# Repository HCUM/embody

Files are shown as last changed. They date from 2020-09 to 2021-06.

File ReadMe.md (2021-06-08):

# EMBody: A Data-Centric Toolkit for EMG-Based Interface Prototyping and Experimentation

This repository contains EMBody, a data-centric toolkit for rapid prototyping and experimentation of EMG-based interfaces. You can find the associated publication [here](https://dl.acm.org/doi/10.1145/3457142). Feel free to watch our short teaser video below. You can additionally find a detailed [instructional video](./manual/manual.mp4) as part of the [manual](./manual).

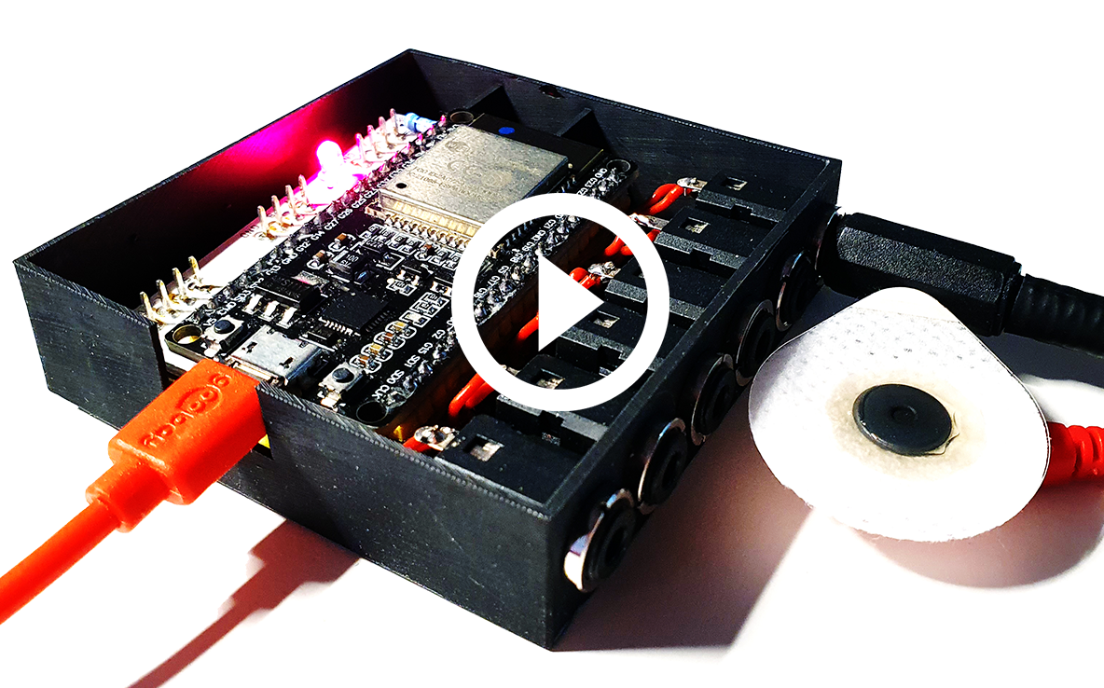
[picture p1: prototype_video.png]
System teaser|70% (https://jakob-karolus.de/publications/karolus21embody.mp4)


## About
EMBody is a toolkit, which is developed at LMU Munich. It is financially supported by the European Union's Horizon 2020 Programme under ERCEA grant no. 683008 AMPLIFY.

The toolkit consists of a hardware prototype that can record electrical potentials (e.g. via surface electrodes), convert these in a digital representation, and stream them over an available WiFi connection. This is complemented by an accompanying [software application](./embody), that receives the signal and provides an interpretation of the data.

EMBody's main use case is recording electromyograms (EMG) via surface electrodes. We envision that the toolkit enables creators to rapidly begin their journey into EMG-based interfaces. This repository contains all the necessary resources to build the system from scratch. Please feel free to contact us in case of questions.

## Hardware ressources
* Circuit board layouts and cases: see [Casing](./casings) and [Circuits](./circuits) for files
* Short [assembly description](./circuits)
* Firmware for ESP32 microcontroller: see [Firmware](./esp_firmware)

## Software application
* python application [EMBody](./embody) connecting to the prototype, see the [Manual](./manual) for a detailed operation manual and workflow including the instructional video

## Citing EMBody

Below are the BibTex entries to cite EMBody
```
@article{karolusEmbody2021,
author = {Karolus, Jakob and Kiss, Francisco and Eckerth, Caroline and Viot, Nicolas and Bachmann, Felix and Schmidt, Albrecht and Wo\'{z}niak, Pawe\l W.},
title = {EMBody: A Data-Centric Toolkit for EMG-Based Interface Prototyping and Experimentation},
year = {2021},
issue_date = {June 2021},
publisher = {Association for Computing Machinery},
address = {New York, NY, USA},
volume = {5},
number = {EICS},
doi = {10.1145/3457142},
url = {https://github.com/HCUM/embody},
journal = {Proc. ACM Hum.-Comput. Interact.},
month = may,
articleno = {195},
numpages = {29}
}
```

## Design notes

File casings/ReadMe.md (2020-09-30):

# Casing files
STL files for the prototype's casing as well as lid to cover the components.
Additionally, a scene file from 3ds Max is provided for customization.

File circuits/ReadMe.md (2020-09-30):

# Circuit files
## INA2321Bioamp_2018-10-30.zip
Gerber files for adapted bio amplifier (see https://github.com/BigCorvus/2-Channel-Biopotential-Amp) and corresponding bom list.
## adapter19to3x4_v3_2020-05-04.zip
Gerber files for custom adapter board connecting three amplifiers to a ESP-32 microcontroller.

# Hardware Assembly Instruction

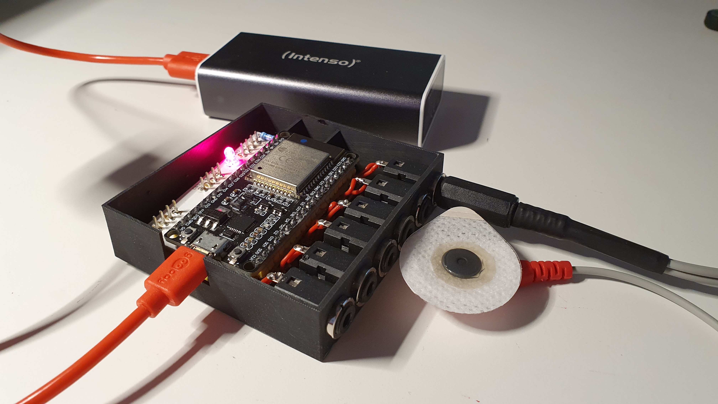
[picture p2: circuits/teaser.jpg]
Wireless EMG Sensor


## General connection diagram

This is the general diagram of the hardware.

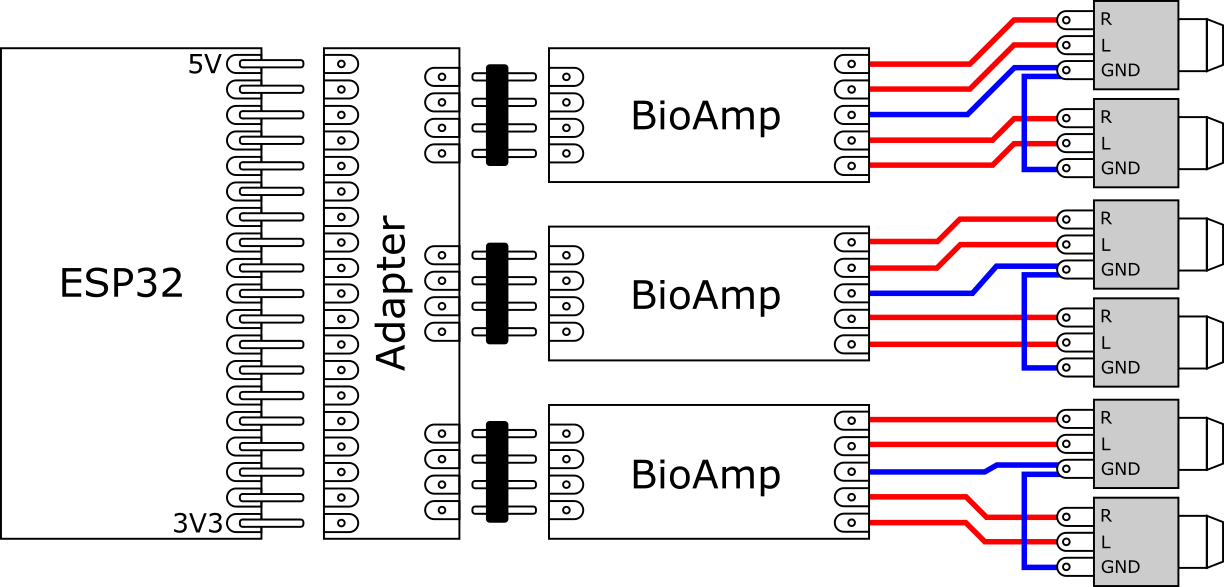
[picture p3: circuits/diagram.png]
Circuit diagram


Follow the instructions below for a guided assembly tutorial.

## How to assemble the EMG hardware
The process is easy and requires minimal skills.
You will need the following tools:

* Soldering iron
* Solder
* Tweezers
* Wire-cutter
* Permanent marker

And the following components:

* ESP32 board x 1
* Bioamplifier x 3
* Adapter board x 1
* Insulated copper wire
* Heat shrink tubing (14mm) 
* LED 5 mm x 1
* 100 Ohm axial resistor x 1
* Header with 4 pins x 3
* Stereo female audio jacks (3.5mm) x 6 - [This model](http://www.farnell.com/datasheets/2645331.pdf) fits in the 3D case
* 3D printed case

### Step 1: solder cables to Bioamplifier board
Cut pieces of cable around 5 cm long, peel one end, and solder them to the five pads on the input side of the Bioamplifier (marked in the image below). The cables should come out on the upper side of the board. Repeat for all Bioamplifier boards.

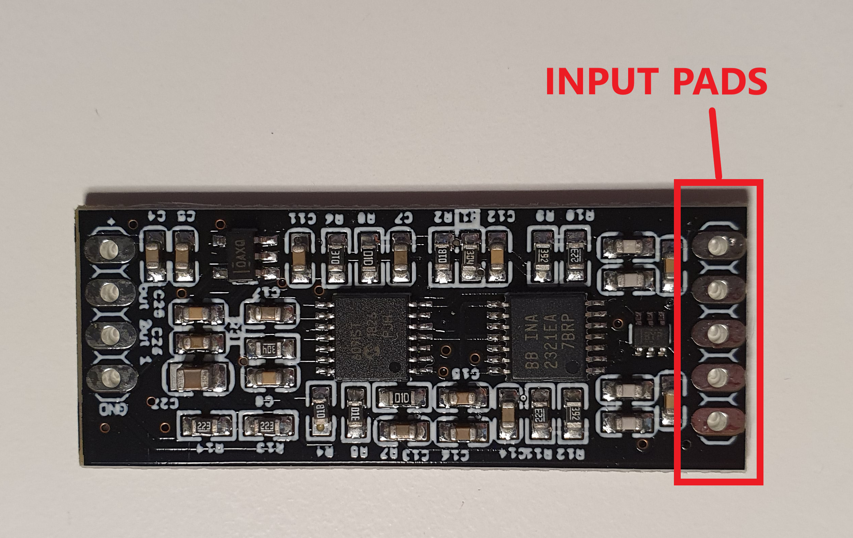
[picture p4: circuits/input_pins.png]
Input pads of the Bioamplifier


### Step 2: insulate the Bioamplifier board
Insert the board through a piece of heat shrink tube of adequate length to cover the components but leaving the pads free. Alternatively, use electrical tape if heat shrink tube is not available. Repeat for all Bioamplifier boards.

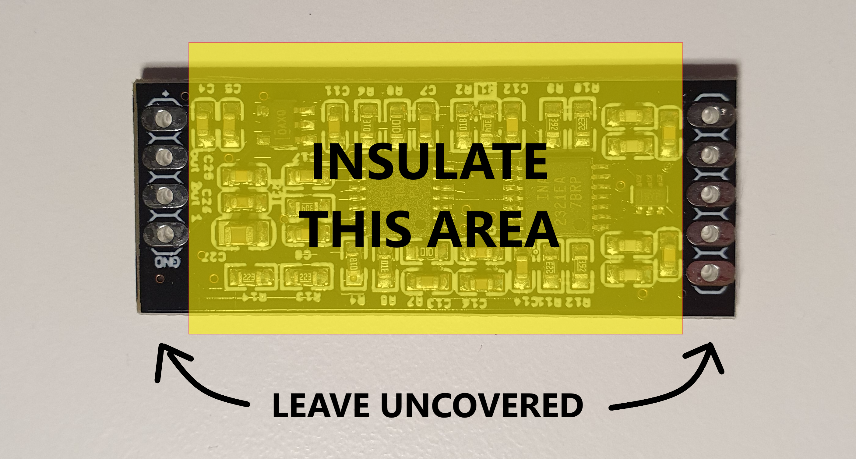
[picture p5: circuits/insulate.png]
Insulate the components


### Step 3: solder headers to Bioamplifier board
Solder the 4-pin headers on the upper side of the board, as shown in the image below. Repeat for all Bioamplifier boards. 

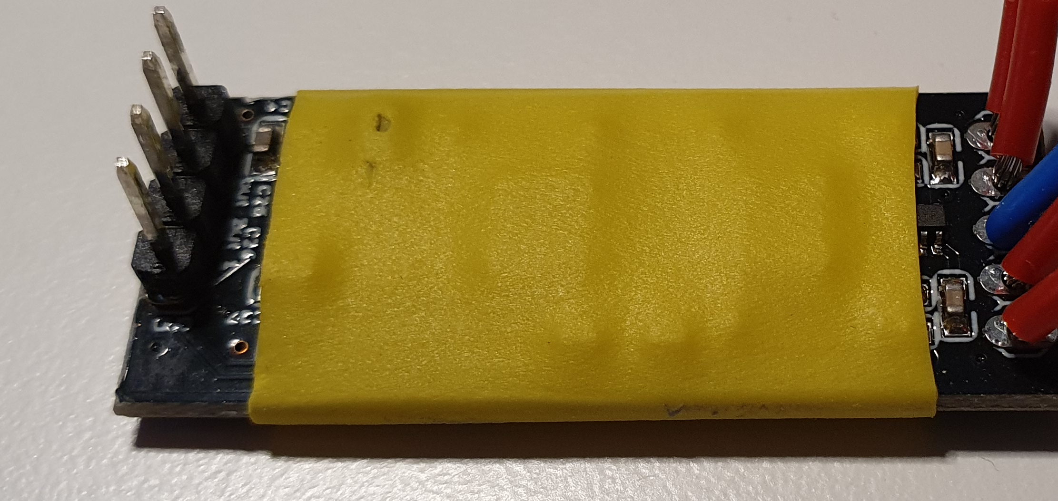
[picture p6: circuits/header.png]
Solder the header pins


### Step 3: solder resistor and LED to Adapter board
Solder the resistor on the upper side of the board, as shown in the picture. Solder the LED on the same side. Remove the protruding pins on the opposite side.

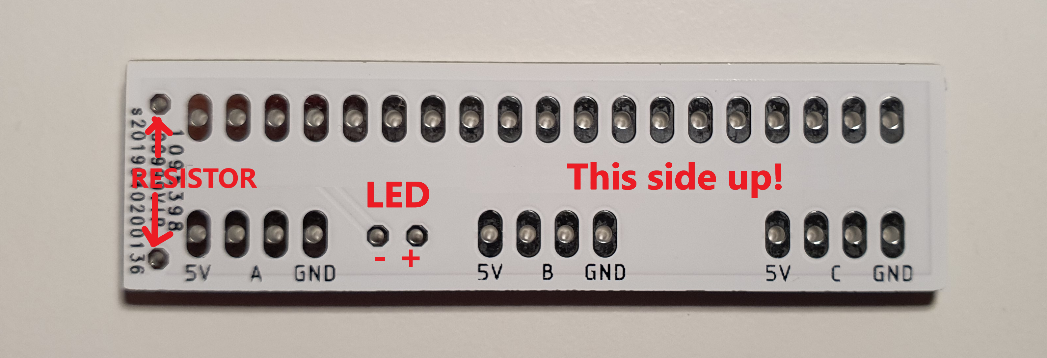
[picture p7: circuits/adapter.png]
Solder LED and resistor


### Step 4: solder ESP32 to Adapter board
Solder the 19 pins of the left side of the ESP32 to the Adapter board (see left image from step 5).

### Step 5: solder Bioamplifiers to the Adapter board
Solder all Bioamplifiers to the Adapter board. The Adapter board should face up, on top of the Bioamplifiers. 

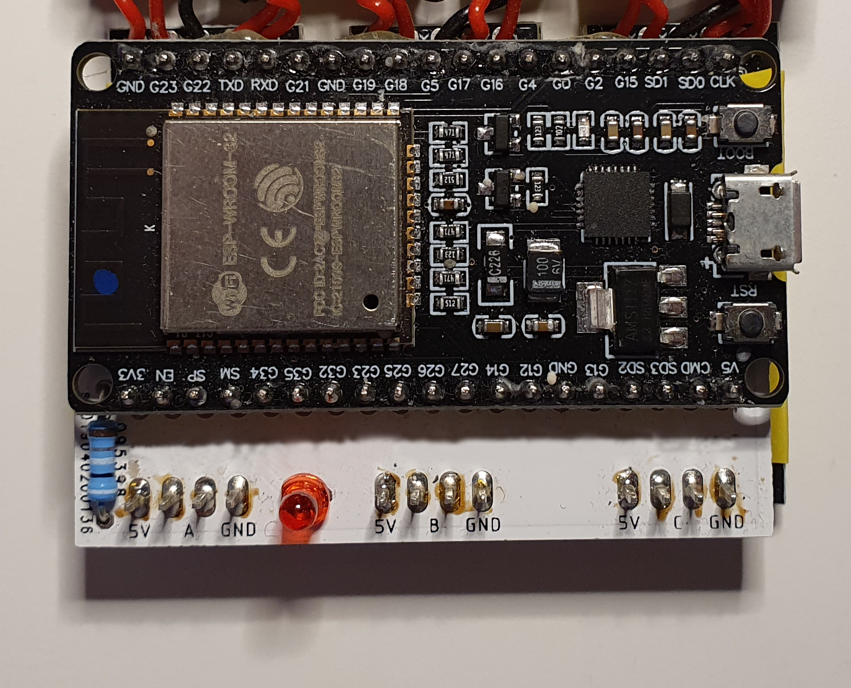
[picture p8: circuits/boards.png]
Top view of assembled boards
||Bottom view of assembled boards|

### Step 6: solder connectors
Position the boards and the audio connectors in the 3D-printed case, and use a permanent marker to mark the length of the wires where they touch the corresponding pad of the connector (use as reference the image from Step 7).
Remove all parts from the case. Cut and peel the cables using the marks as reference. Using additional pieces of wire, solder the ground pin of the audio connectors together in pairs, so you have three pairs of connectors. Solder the cables from the Bioamplifiers to the connectors.

### Step 7: flash and finish
Position the hardware in the case, as shown in the image below.
Close the case. The device is ready to flash! 

Finished device

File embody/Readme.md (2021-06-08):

# EMBody software application

**For a complete manual on EMBody's workflow, please refer to the [Manual](../manual), which also includes an instructional video.**

Run "python Main.py" to start the application. This software is based on Python 3.6 and the following libraries: 
* wxPython
* matplotlib
* pandas
* numpy
* scipy
* sklearn
* pylsl

It provides a GUI split into different views, that interact with each other: Setup, Calibration and Liveview, as well as a logic backend for stream and classification handling, communicating over StreamEvents.
Note that developers can provide additional functionality by adding more views or substituting stream handling (StreamHandler.py). Of special interest in this case should also be the ClassificationManager.py handling classification for the incoming signal.
Developers are encouraged to change preprocessing, feature generation and classification algorithms if needed.

## Overview of EMBody's classification pipeline
Please refer to the paper and source code for additional information.

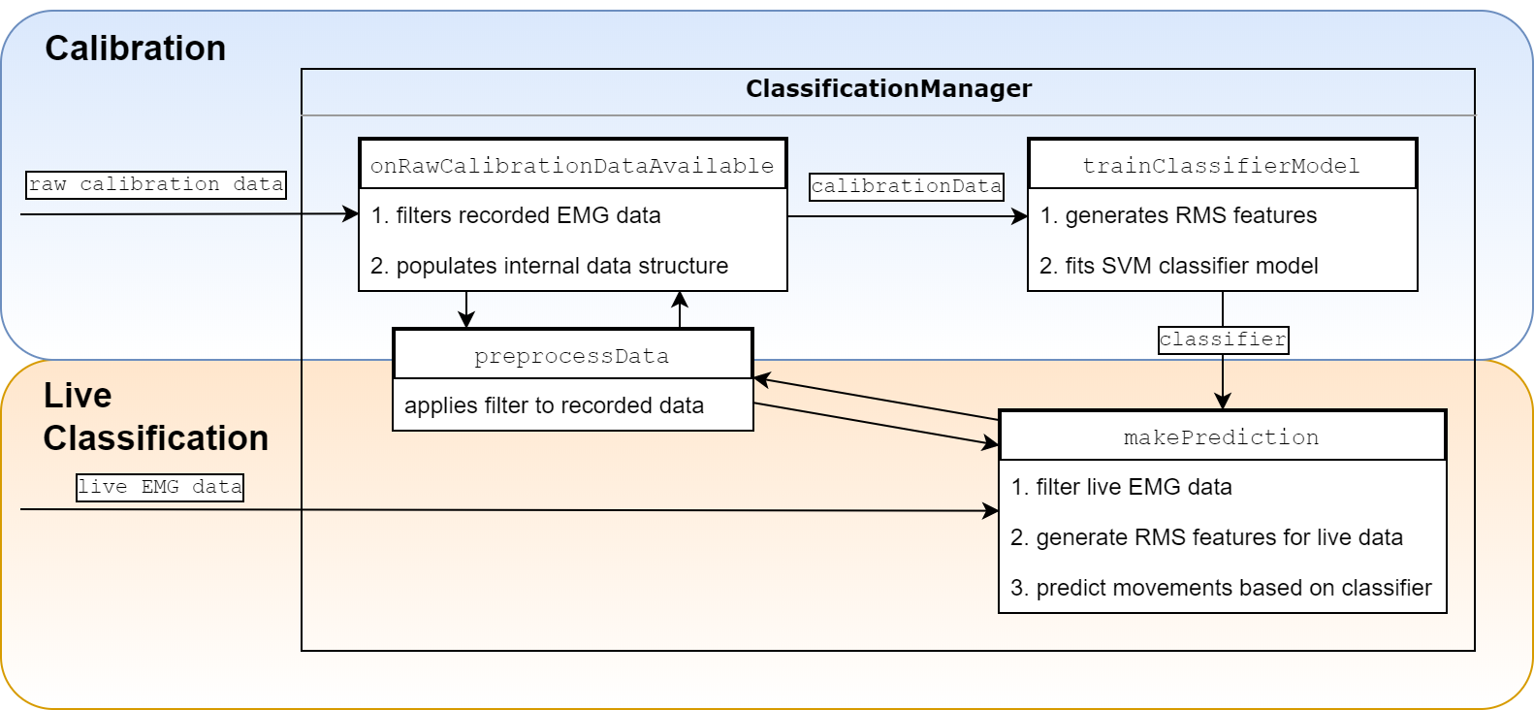
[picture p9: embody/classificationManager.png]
classificationManager


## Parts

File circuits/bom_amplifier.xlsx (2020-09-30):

Designator | Manufacturer Part Number | Quantity
R7, R8 | RC0603FR-07100KL | 2
C4, C5, C11, C15, C26 | CC0603KRX7R9BB104 | 5
C1, C2, C6, C9 | CC0603JRNPO9BN101 | 4
C3, C10, C25 | CC0603KRX7R9BB103 | 3
C27 | CC0805KKX5R8BB106 | 1
R5, R6 | RC0603FR-071ML | 2
R2, R4 | RC0603FR-071KL | 2
C8, C12 | CC0603KRX7R9BB102 | 2
C7, C13, C14, C16, C17 | CC0603KRX7R8BB105 | 5
R10, R11, R13, R14 | RC0603FR-0722KL | 4
R1, R3 | 0603SAF3003T5E | 2
R9, R12 | RC0603FR-073K9L | 2
U$1 | INA2321EA/250 | 1
U$3 | MCP609-I/ST | 1
IC2 | OPA333AIDBVT | 1
U$2 | TPD4E1B06DCKR | 1

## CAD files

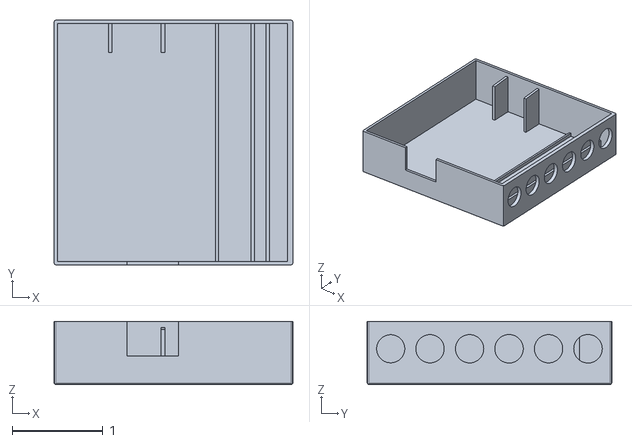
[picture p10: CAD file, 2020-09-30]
casings/emg_case_bottom.STL
2.63 x 2.69 x 0.694

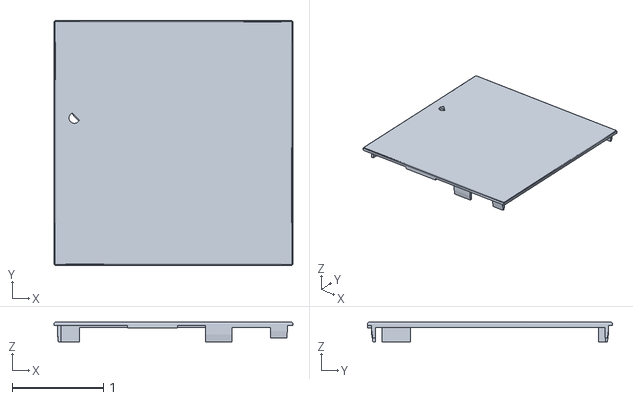
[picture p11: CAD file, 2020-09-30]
casings/emg_case_lid.STL
2.62 x 2.69 x 0.217

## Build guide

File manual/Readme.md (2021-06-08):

# EMBody: An Integrated Toolkit for EMG-Based Interface Prototyping

This manuals describe how to use the software toolkit to connect to an existing EMBody prototype and interpret the signal.
The software is based on Python 3.6 and the following libraries: wxPython, matplotlib, pandas, numpy, scipy, sklearn, pylsl (also refer to [EMBody Software](../embody)).
It provides a GUI split into different views, that interact with each other: Setup, Calibration and Liveview, as well as a logic backend for stream and classification handling, communicating over StreamEvents. Note that developers can provide additional functionality by adding more views or substituting stream handling (StreamHandler.py). Of special interest in this case should also be the ClassificationManager.py handling classification for the incoming signal. Developers are encouraged to change preprocessing, feature generation and classification algorithms if needed.
Details on hook methods and their purpose can be found in the paper (an overview is provided at [EMBody Software](../embody)).

EMBody already provides out-of-the-box functionality to calibrate and predict gestures recorded via EMG signals. This section outlines a typical workflow and gives detailed instructions for the individual views of the toolkit. The following video provides the same step by step guide for this workflow.

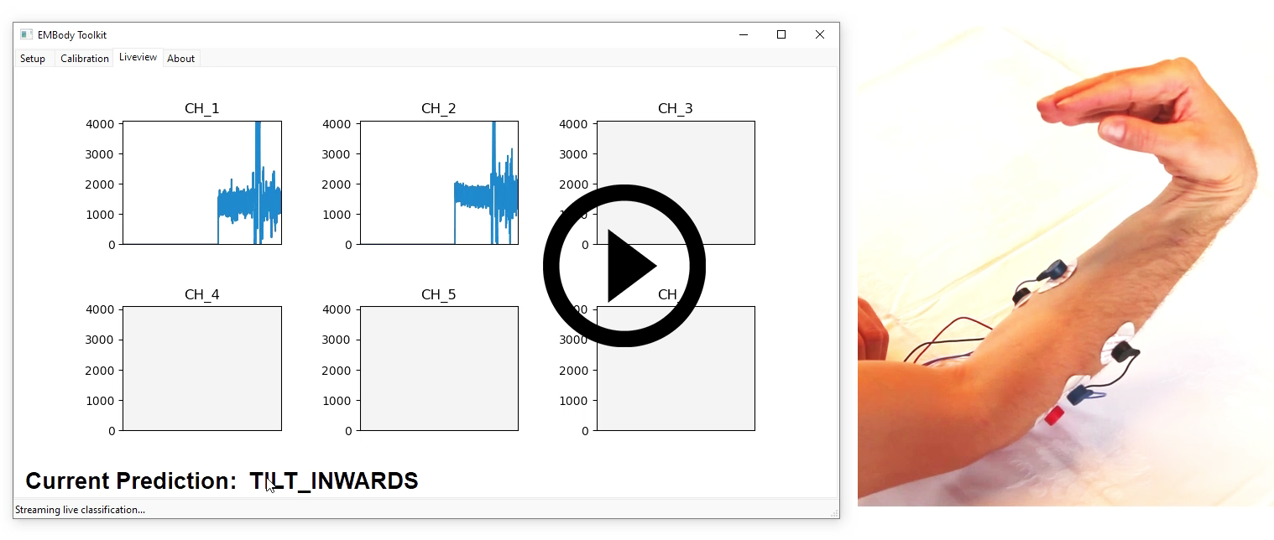
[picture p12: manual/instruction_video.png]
System teaser|50% (https://jakob-karolus.de/videos/embody_manual.mp4)


## Standard Workflow
1. Set-up prototype and connect electrodes, see **Electrode Setup**.
2. Connect to prototype via **Connection Setup**. Select active channels and hit calibrate.
3. Provide a list of gestures/movements to recognize in **Calibration**.
4. Run a complete calibration providing sample data for each gesture.
5. Train a classifier model.
6. Start live classification, enabling a UDP stream (port: 3334) of live predictions (alternatively: pylsl).
7. Connect to the live classification stream with any other application and use for interaction.

## Electrode Setup
The EMBody prototype uses a bipolar sensing technique (two sensing electrodes, one GND/REF electrode) to reduce noise artifacts. Identify suitable muscle groups to record first (also see the EMBody video).
Place the GND electrode nearby, but on a non-involved area (e.g. close to bones or on fat tissue). For forearm recordings, a position close (but not on the elbow, due to movement artifacts) is advised.
Eventually, place the two sensing electrodes over the muscle belly that you are interested in. Repeat these steps for any muscle (group) required (EMBody supports up to six channels).

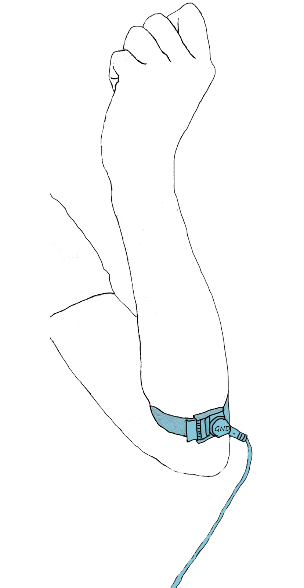
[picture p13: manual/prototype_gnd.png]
prototype_gnd
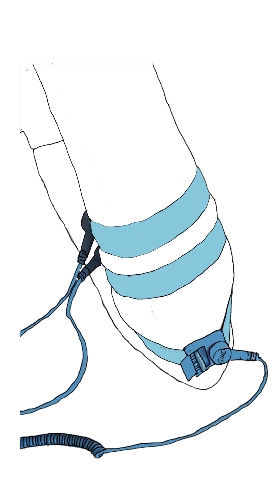
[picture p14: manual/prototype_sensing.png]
prototype_sensing
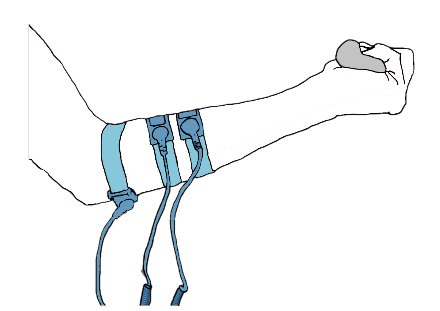
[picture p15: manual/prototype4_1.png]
prototype_sensing4_1
|  |  | 
|:--:|:--:| 
| *Connecting GND electrode* | *Connecting sensing electrodes* |

### General guidelines for electrode placement
* Place the GND/REF electrode close by, but on uninvolved tissue. Bones and fat tissue are good candidates.
* For bipolar measurements, noise is cancelled out through differential measurments:
  * Electrodes close together reduces environmental noise (any electromagnetic noise), but also dimishes signal discriminativeness.
  * Likewise, the farther apart the sensing electrodes are, the bigger the noise impact. It also decrease locality of the signal (harder to pinpoint individual muscles).
  * A good trade-off is to cover approx. 50% of the muscle belly with distance between the electrodes.
* Unipolar measurements (one sensing, one ref electrode) are supported as well, as long as the sent out UDP stream adheres to the correct format ("timestamp;CH_1;CH_2;..."). Note that the software can technically handle more than six channels, but only display up to six in the live view.
* The size of the electrode greatly impacts the recorded signal. The effect is similar to changing amplifier gain.
  * Small diameter electrodes can provide a more localized signal, but provide a smaller amplitude.
  * Bigger diameter "capture more signal", hence provide higher amplitude.

Finally, connect the electrode cables to the hardware prototype and power it, e.g. via a powerbank. Be sure to configure its Wi-Fi settings in advance (see next section).

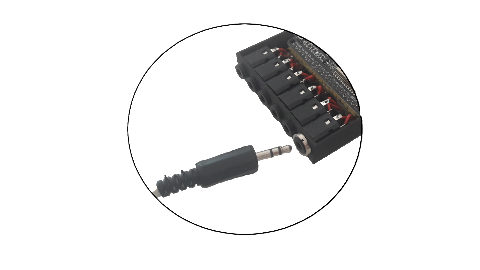
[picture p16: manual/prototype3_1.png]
prototype3_1
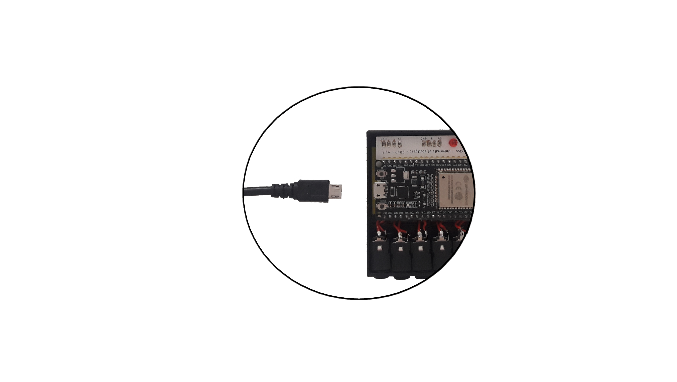
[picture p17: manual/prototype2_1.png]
prototype2_1
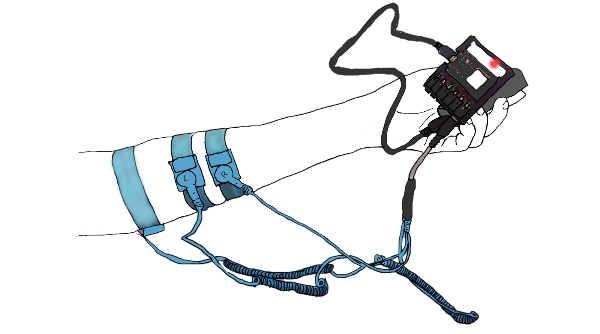
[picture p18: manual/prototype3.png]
prototype3
|   | 
|:--:|
| *Connecting electrode cables and power* |

### Wi-Fi Setup (once)
The standard firmware implements a config portal for Wi-Fi settings.
If no SSID was previously registered, the config portal boots up automatically. Connect to the SSID "EMG_xxx" (where xxx is the Chip ID of your microcontroller) and use "emg" as password.
Navigate to "192.168.4.1" and configure Wi-Fi settings. On subsequent boot-ups, the microcontroller will try to connect to the provided configuration (Config portal boot can be forced by pressing the BOOT button).

## Connection Setup
After starting the EMBody software application (make sure to install required python packages, e.g. via "pip install <package_name>"), you can connect to the prototype (or any other UDP stream, see above) via the Setup tab.
The setup tab specifies connection properties, like UDP address/port and channels to use. It includes a testing mechanism for given UDP connections. If the prototype and the receiving computer are on the same network a blank address (corresponding to "**0.0.0.0**") is sufficient. Note that the prototype uses **port 3333** by default.
After specifying a connection and succesfully testing it, the toolkit provides information about detected channels and an estimated sampling rate. 

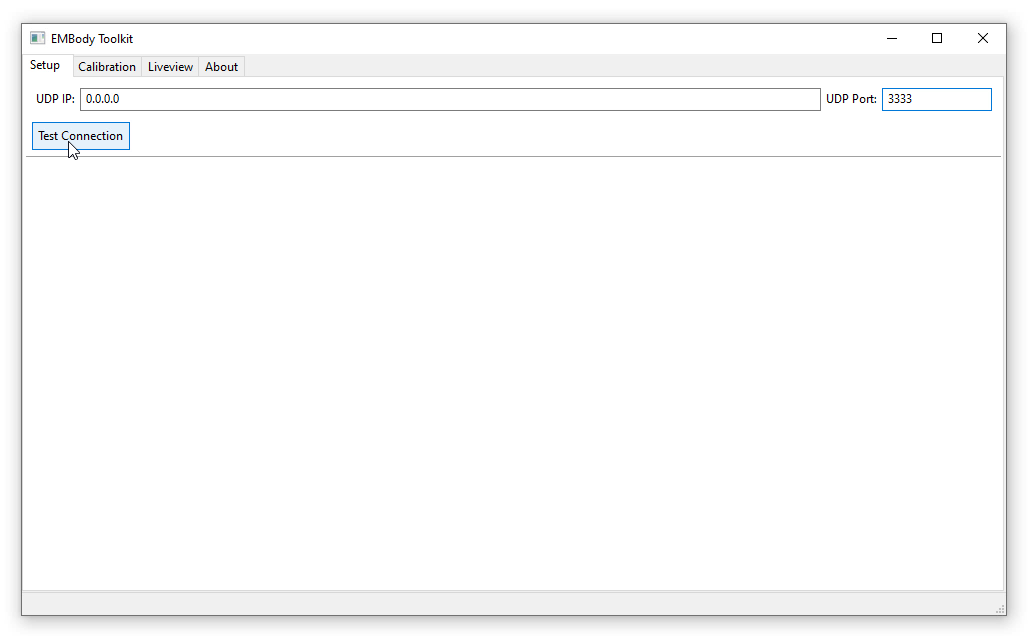
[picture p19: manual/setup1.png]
setup1
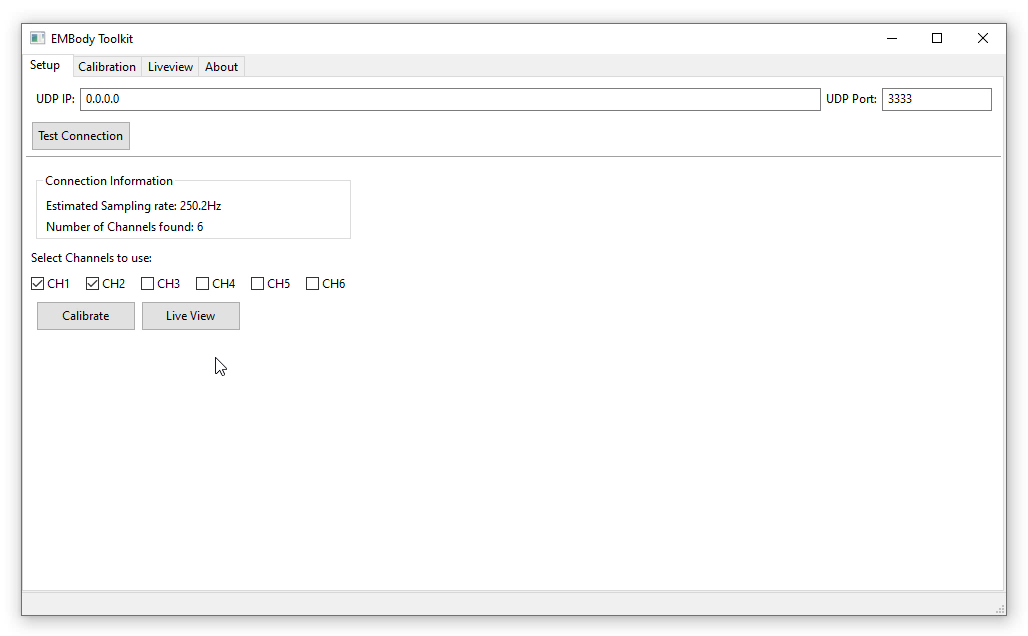
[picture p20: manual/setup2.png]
setup2
|  |  | 
|:--:|:--:|
| *Specifying connection* | *Checking connection info and selecting channels* |

If you are using a custom prototype sending UDP packages, make sure to adhere to the protocol (or adapt the StreamHandler.py). Note that the algorithm expects a timestamp channel on the first position, followed by data channels: timestamp;CH_1;CH_2;....
Aferwards, users can decide which channels to activate and either jump to the calibration procedure (**Calibration**) or just display the signal in the live view (**Liveview**).

## Calibration
To recognize and predict performed gestures, the users needs to provide the toolkit with exemplary data for each to-be-recognized gesture (calibration label) or movement. Note that the toolkit performs best for static gestures (e.g., forming a fist, tilting the hand left/right). On the left side, you may provide one calibration label per line (a null class is automatically added) or load/save an existing list of labels (icon top left). *Create Calibration* will construct an empty datastructure (on the right side) showing you for which labels you will calibrate for.

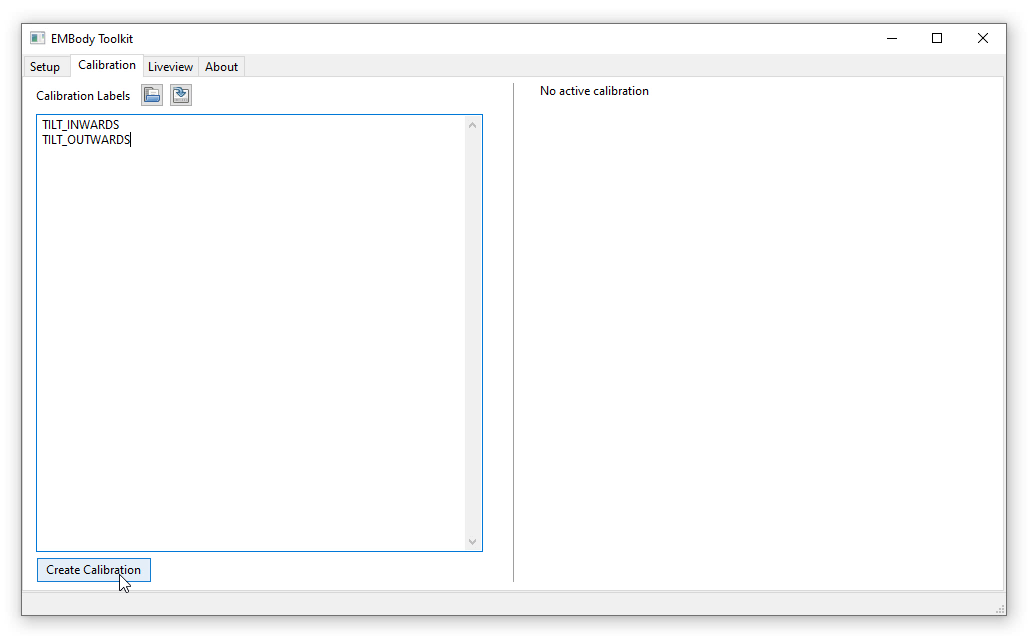
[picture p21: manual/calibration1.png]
calibration1
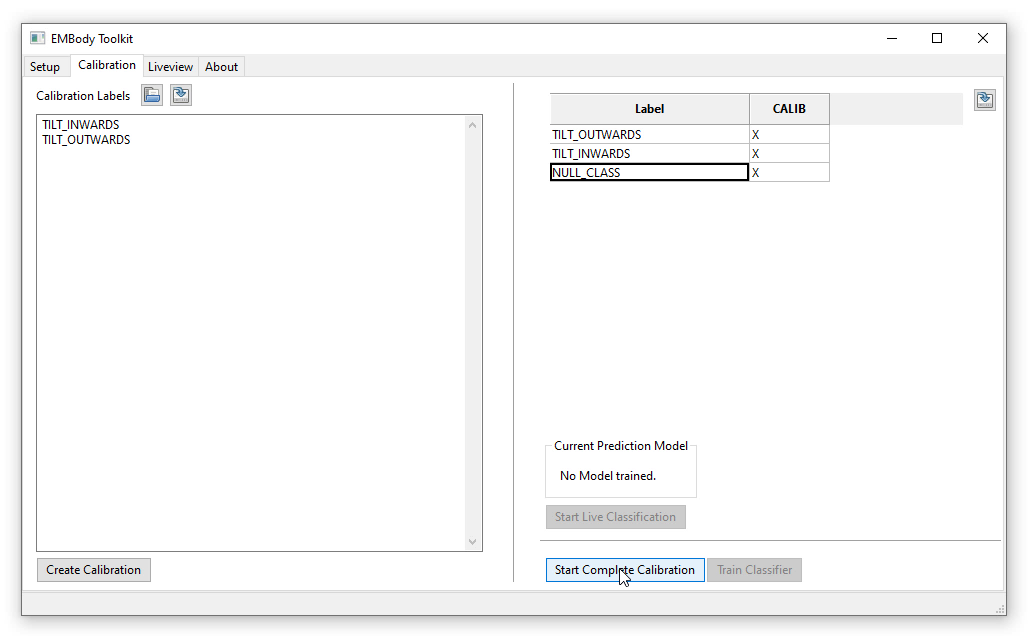
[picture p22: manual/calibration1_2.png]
calibration1_2
|  |  | 
|:--:|:--:|
| *Specifying calibration labels* | *Creating an empty calibration (right side)* |

*Start Complete Calibration* will guide you through a full calibration process, where you will alternatingly provide sample data for the labels. After the process completes, the toolkit displays the amount of collected data (in seconds) for each label and allows the user to train a classification. Depending on the size of collected data, this might take a while and happens in the background. After completion, the software will perform a 10-fold cross validation on the learned model to indicate its performance. Upon succesfully training a model, the user can start a live classification (the current model used will be displayed in the calibration tab). The live classification is available in the **Liveview** tab as well as will be streamed via UDP (**port: 3334**), thus being available to any other software in the network. The port can be specified (not shown in the picture). Alternatively, EMBody provides streaming over lab streaming layer (LSL) as well, see pylsl. Note that at any point you can save a recorded calibration for post-hoc analysis (top right), e.g., running different classification schemes.

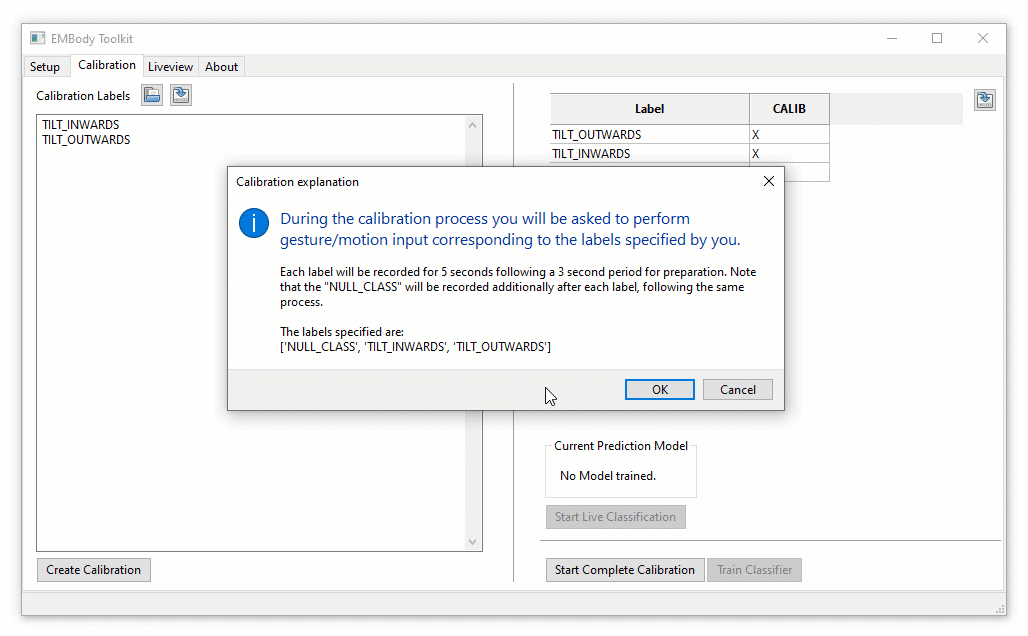
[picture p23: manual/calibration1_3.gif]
calibration1_3
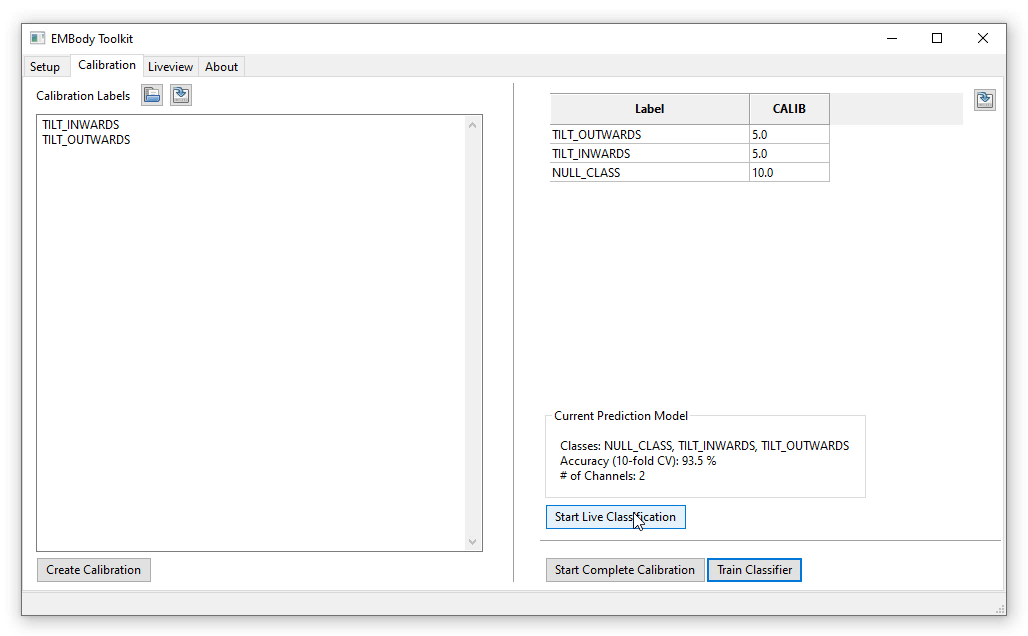
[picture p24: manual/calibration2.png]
calibration2
|  |  | 
|:--:|:--:|
| *Wizard during calibration* | *After training a classifier (model information on bottom right)* |

## Liveview
This view will display the live signal coming from the prototype (upon connecting to it). Note that it will mimick the selected active channels in the **Setup** tab. If a trained model is available and live classification is active, this tab will also display the currently detected gesture.

| liveview  | 
|:--:|
| *Liveview of channels 1 and 2, including live classification for incoming EMG data* |

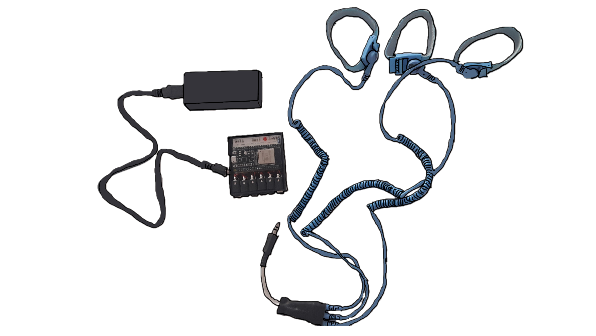
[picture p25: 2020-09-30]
manual/prototype1.png

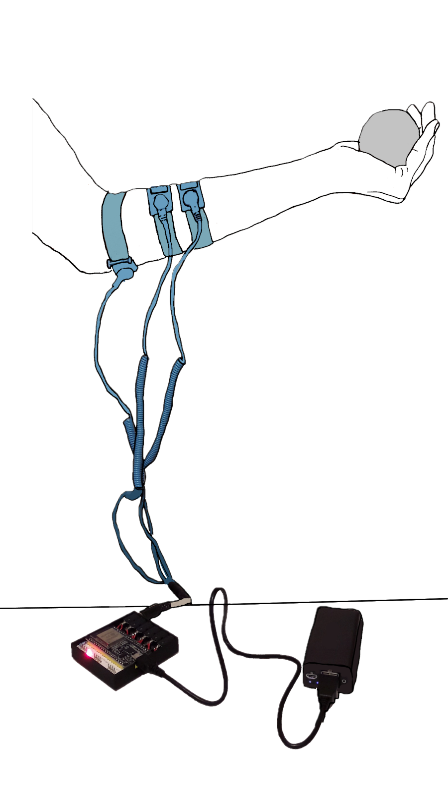
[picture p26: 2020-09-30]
manual/prototype4.png

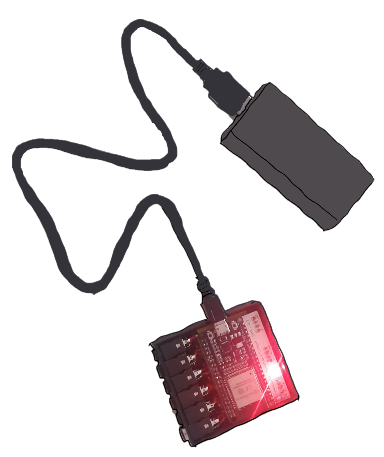
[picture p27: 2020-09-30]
manual/prototype2.png

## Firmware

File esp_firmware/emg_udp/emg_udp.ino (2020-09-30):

#include <esp_wifi.h>
#include <WiFi.h>
#include <WiFiUdp.h>
#include <WiFiClient.h>
#include <ESP_WiFiManager.h>

#define ESP_getChipId()   ((uint32_t)ESP.getEfuseMac())
#define PERIODE    4L //equals to 250Hz sampling rate -> adjust if higher sampling rate is required

// SSID and PW for Config Portal
String ssid = "EMG_" + String(ESP_getChipId(), HEX);
const char* password = "emg";

// SSID and PW for your Router
String Router_SSID;
String Router_Pass;


//sensor pins, change to your configuration if needed
#define SENSOR_PIN_1 32
#define SENSOR_PIN_2 33
#define SENSOR_PIN_3 34
#define SENSOR_PIN_4 35
#define SENSOR_PIN_5 36
#define SENSOR_PIN_6 39

//broadcasting
IPAddress udpAddress; //gets assigned when connected to a network
const uint udpPort = 3333; //adjust if port is n/a

//sensor values
int value1;
int value2;
int value3;
int value4;
int value5;
int value6;
unsigned long time1;

WiFiUDP udp;
boolean connected = false;

//trigger for config
const int TRIGGER_PIN = 0;

// Indicates whether ESP has WiFi credentials saved from previous session
bool initialConfig = false;

void setup() 
{
  // initialize the LED digital pin as an output.
  pinMode(TRIGGER_PIN, INPUT_PULLUP);
  pinMode(SENSOR_PIN_1, INPUT);
  pinMode(SENSOR_PIN_2, INPUT);
  pinMode(SENSOR_PIN_3, INPUT);
  pinMode(SENSOR_PIN_4, INPUT);
  pinMode(SENSOR_PIN_5, INPUT);
  pinMode(SENSOR_PIN_6, INPUT);
  Serial.begin(115200);
  Serial.println("\nStarting");

  unsigned long startedAt = millis();
  
  ESP_WiFiManager ESP_wifiManager("ConfigOnSwitch");
  ESP_wifiManager.setMinimumSignalQuality(-1);

  //check for previous credentials
  Router_SSID = ESP_wifiManager.WiFi_SSID();
  Router_Pass = ESP_wifiManager.WiFi_Pass();
  ssid.toUpperCase();
  
  if (Router_SSID == "")
  {
    Serial.println("We haven't got any access point credentials, so get them now");   
    //it starts an access point 
    //and goes into a blocking loop awaiting configuration
    if (!ESP_wifiManager.startConfigPortal((const char *) ssid.c_str(), password)) 
      Serial.println("Not connected to WiFi but continuing anyway.");
    else 
      Serial.println("WiFi connected...yeey :)");    
  }

  #define WIFI_CONNECT_TIMEOUT        30000L
  #define WHILE_LOOP_DELAY            200L
  #define WHILE_LOOP_STEPS            (WIFI_CONNECT_TIMEOUT / ( 3 * WHILE_LOOP_DELAY ))
  
  startedAt = millis();
  
  while ( (WiFi.status() != WL_CONNECTED) && (millis() - startedAt < WIFI_CONNECT_TIMEOUT ) )
  {   
    WiFi.mode(WIFI_STA);
    WiFi.persistent (true);
    // We start by connecting to a WiFi network
  
    Serial.print("Connecting to ");
    Serial.println(Router_SSID);

    //register for WiFiEvents
    WiFi.onEvent(WiFiEvent);
    WiFi.begin(Router_SSID.c_str(), Router_Pass.c_str());

    int i = 0;
    while((!WiFi.status() || WiFi.status() >= WL_DISCONNECTED) && i++ < WHILE_LOOP_STEPS)
    {
      delay(WHILE_LOOP_DELAY);
    }    
  }

  Serial.print("After waiting ");
  Serial.print((millis()- startedAt) / 1000);
  Serial.print(" secs more in setup(), connection result is ");

  if (WiFi.status() == WL_CONNECTED)
  {
    Serial.print("connected. Local IP: ");
    Serial.println(WiFi.localIP());

  }
  else
    Serial.println(ESP_wifiManager.getStatus(WiFi.status()));
}


//wifi event handler
void WiFiEvent(WiFiEvent_t event) {
  switch (event) {
    case SYSTEM_EVENT_STA_GOT_IP:
      //When connected set
      Serial.print("WiFi connected! IP address: ");
      Serial.println(WiFi.localIP());
      //initializes the UDP state
      udp.begin(WiFi.localIP(), udpPort);
      assignBroadcastAddress();
      //This initializes the transfer buffer
      connected = true;
      break;
    case SYSTEM_EVENT_STA_DISCONNECTED:
      Serial.println("WiFi lost connection");
      connected = false;
      break;
  }
}

void assignBroadcastAddress(void){
  udpAddress = WiFi.localIP();
  udpAddress[3] = 255;
}

void loop()
{
  ulong roundtime = millis();
  // is configuration portal requested?
  if (digitalRead(TRIGGER_PIN) == LOW) {
    doConfig();
  }
   
  //only send data when connected
  if (connected) {
    sendPacket();
  }
  //Wait for a total time of approx. 4 milliseconds to ensure 250Hz
  while((millis() - roundtime) < PERIODE);
}

void doConfig(void){
    Serial.println("\nConfiguration portal requested.");
    
    ESP_WiFiManager ESP_wifiManager;
    Serial.print("Opening configuration portal. ");
    
    //Check if there is stored WiFi router/password credentials.
    Router_SSID = ESP_wifiManager.WiFi_SSID();
    if (Router_SSID != ""){
      Serial.println("Got stored Credentials. No timeout");
    }
    else{
      Serial.println("No stored Credentials. No timeout");
    }

    //start config
    if (!ESP_wifiManager.startConfigPortal((const char *) ssid.c_str(), password)){
      Serial.println("Not connected to WiFi but continuing anyway.");
    } 
    else{
      //if you get here you have connected to the WiFi
      Serial.println("connected.");
    }
}

void sendPacket(void){
    //read out all channels to allow for time-consistent values
    value1 = analogRead(SENSOR_PIN_1);
    value2 = analogRead(SENSOR_PIN_2);
    value3 = analogRead(SENSOR_PIN_3);
    value4 = analogRead(SENSOR_PIN_4);
    value5 = analogRead(SENSOR_PIN_5);
    value6 = analogRead(SENSOR_PIN_6);
    time1 = millis();

    //remove if sampling rate is of importance
    delayMicroseconds(500);
    
    udp.beginPacket(udpAddress, udpPort);
    udp.printf("%lu;%u;%u;%u;%u;%u;%u", time1, value1, value2, value3, value4, value5, value6);
    udp.endPacket();
    delayMicroseconds(500);
}

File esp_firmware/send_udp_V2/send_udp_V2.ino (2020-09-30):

#include <WiFi.h>
#include <WiFiUdp.h>

// WiFi network name and password:
//TODO: update network credentials if needed
const char * networkName = "TODO";
const char * networkPswd = "TODO";

//sensor pin
#define SENSOR_PIN_1 32
#define SENSOR_PIN_2 33
#define SENSOR_PIN_3 34
#define SENSOR_PIN_4 35
#define SENSOR_PIN_5 36
#define SENSOR_PIN_6 39

#define PERIODE    4L //equals to 250Hz sampling rate -> adjust if higher sampling rate is required


//IP address to send UDP data to:
// either use the ip address of the server or
// a network broadcast address
//TODO: update if needed
//broadcast
const char * udpAddress = "x.x.x.255";
const int udpPort = 3333;

//Are we currently connected?
boolean connected = false;

//sensor value
int value1;
int value2;
int value3;
int value4;
int value5;
int value6;
unsigned long time1;

//The udp library class
WiFiUDP udp;

void setup() {
  // Initilize hardware serial:
  Serial.begin(115200);
  pinMode(SENSOR_PIN_1, INPUT);
  pinMode(SENSOR_PIN_2, INPUT);
  pinMode(SENSOR_PIN_3, INPUT);
  pinMode(SENSOR_PIN_4, INPUT);
  pinMode(SENSOR_PIN_5, INPUT);
  pinMode(SENSOR_PIN_6, INPUT);

  //Connect to the WiFi network
  connectToWiFi(networkName, networkPswd);
}

void loop() {
  ulong roundtime = millis();
   
  //only send data when connected
  if (connected) {
    sendPacket();
  }
  //Wait for a total time of approx. 4 milliseconds to ensure 250Hz
  while((millis() - roundtime) < PERIODE);
}

void sendPacket(void){
    //read out all channels to allow for time-consistent values
    value1 = analogRead(SENSOR_PIN_1);
    value2 = analogRead(SENSOR_PIN_2);
    value3 = analogRead(SENSOR_PIN_3);
    value4 = analogRead(SENSOR_PIN_4);
    value5 = analogRead(SENSOR_PIN_5);
    value6 = analogRead(SENSOR_PIN_6);
    time1 = millis();

    //remove if sampling rate is of importance
    delayMicroseconds(500);
    
    udp.beginPacket(udpAddress, udpPort);
    udp.printf("%lu;%u;%u;%u;%u;%u;%u", time1, value1, value2, value3, value4, value5, value6);
    udp.endPacket();
    delayMicroseconds(500);
}

void connectToWiFi(const char * ssid, const char * pwd) {
  Serial.println("Connecting to WiFi network: " + String(ssid));

  // delete old config
  WiFi.disconnect(true);
  //register event handler
  WiFi.onEvent(WiFiEvent);

  //Initiate connection
  WiFi.begin(ssid, pwd);

  Serial.println("Waiting for WIFI connection...");
}

//wifi event handler
void WiFiEvent(WiFiEvent_t event) {
  switch (event) {
    case SYSTEM_EVENT_STA_GOT_IP:
      //When connected set
      Serial.print("WiFi connected! IP address: ");
      Serial.println(WiFi.localIP());
      //initializes the UDP state
      //This initializes the transfer buffer
      udp.begin(WiFi.localIP(), udpPort);
      connected = true;
      break;
    case SYSTEM_EVENT_STA_DISCONNECTED:
      Serial.println("WiFi lost connection");
      connected = false;
      break;
  }
}

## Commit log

2020-09-30 initial commit for updated EMBody toolkit
    [bom_amplifier.xlsx, emg_case_bottom.STL, emg_case_lid.STL]
2020-10-01 fixed visual glitch during calibration
